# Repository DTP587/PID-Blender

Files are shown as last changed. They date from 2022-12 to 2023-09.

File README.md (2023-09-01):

# PID Blender
_Blender with PID Speed Control, Build Notes. Part of the Open Science Framework repository [OpenLPE](https://osf.io/evupy/)_

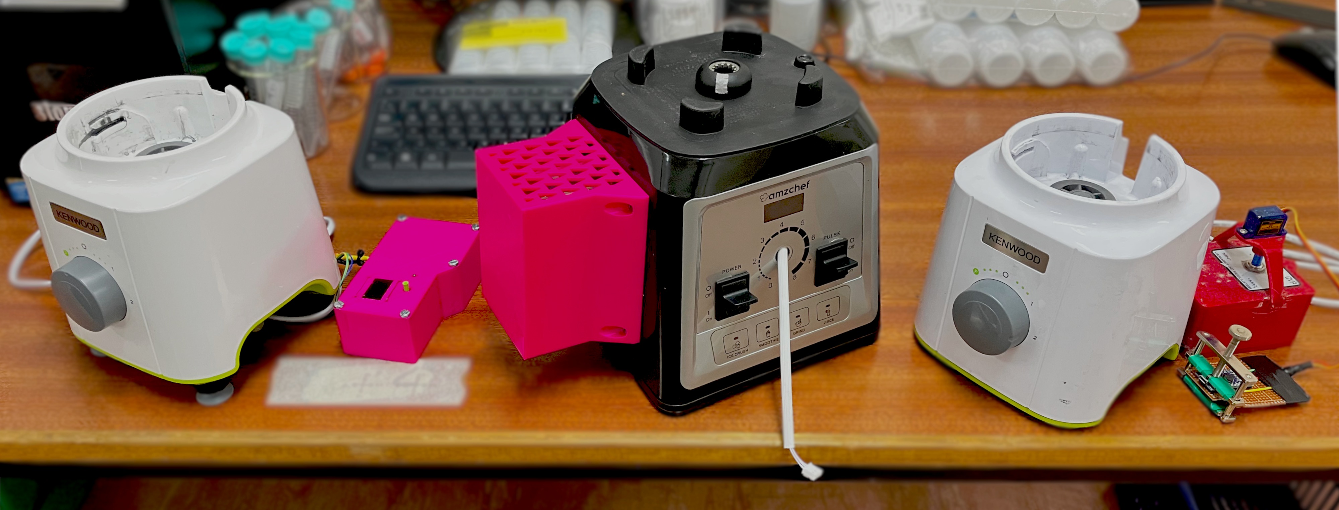
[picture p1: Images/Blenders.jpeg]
Image of all three blenders in order


_From right to left, Dimmer-Blender v1, Dimmer-Blender v2, PID-Blender._

### Background \& Motivation

_This is part of the [OpenLPE](https://osf.io/evupy/) labware project._

For my current work, I needed a blender that could be operated with good control over the exact impeller speed. Initially, I wired dimmer switch into a typical household blender, but found that it was incredibly difficult to maintain the speed accurately and repeatably, especially at low speeds (< $6000$ $rpm$). To improve performance, it was clear what was required was a system that could control the speed dynamically.

The blenders I have been controlling range between $600$ $W$ to $2$ $kW$ peak power, which they can sustain for a maximum of $\approx 1$ $min$ before they get dangerously hot (and melt-y). Some come with automatic sensors to detect when they are overheating and shut-off automatically to save the motor. From my testing, I recommend following the manufacturer's recommendations alternating running it for $1$ $min$ **ON** with a subsequent minimum of $1$ $min$ **OFF** to allow it to cool down.

### Disclaimer!

Playing with AC is _incredibly_ dangerous. Make sure to take all precautions when making modifications and ensure everything is unplugged and grounded.

## Potential Changes

List of changes and whether they have been implemented.

- [ ] The lid to the box doesnt fit the screen perfectly.
- [ ] The $60$ $rpm$ resolution is a bit of a pain at low speeds and could be rectified by switching dynamically between a time-between-counts based approach to measuring speed versus the current counts-within-time.
- [ ] The EMI produced when turning the AC on and off can wreak havoc on the onboard electronics in the box. The arduino needs better isolation from the dimmer module (probably with some well placed tin foil).

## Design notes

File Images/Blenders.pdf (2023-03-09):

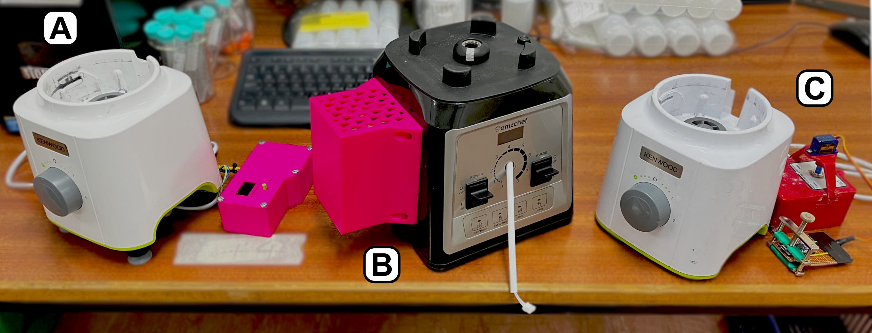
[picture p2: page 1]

A

B

C

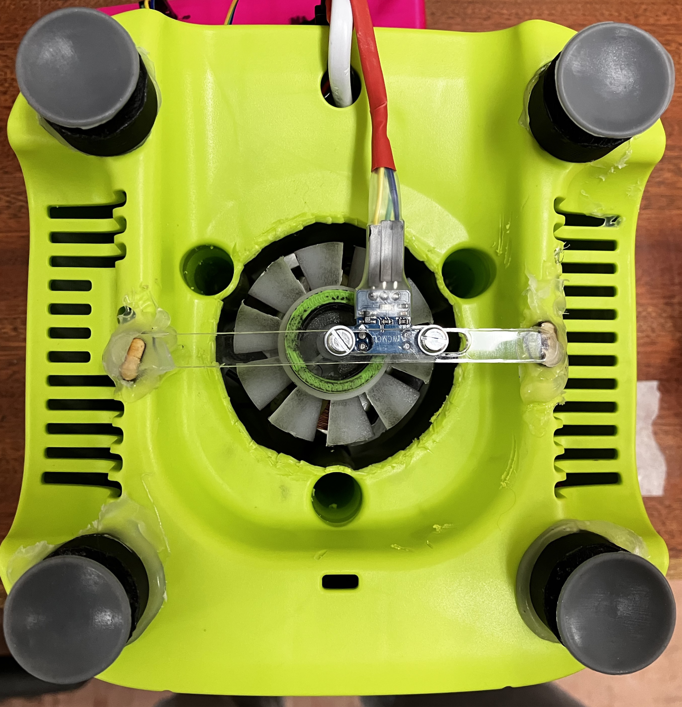
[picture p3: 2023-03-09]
Images/Encoder_Modifications.png

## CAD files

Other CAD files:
CAD/Blender_Box.f3d
CAD/Blender_Feet_Extenders.f3d
CAD/Encoder_Mount.f3d
CAD/Encoder_Ring.f3d

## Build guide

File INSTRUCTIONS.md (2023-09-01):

# Build Instructions and Notes

### Operating Principles

I find that this project has used nearly all the interrupts with this Arduino. It would also be nice if there was some sort of 5V power supply from the blender ([Which is a feature on some of the more pricey models](https://www.amazon.co.uk/Smoothie-AMZCHEF-Commercial-Container-25000RPM/dp/B08CKTB6Z4/ref=sr_1_6?crid=3VN5BPYJ9QWY7&keywords=2000w%2Bblender&qid=1670790024&s=kitchen&sprefix=2000W%2B%2Ckitchen%2C72&sr=1-6&th=1), [or the knock-off alternative](https://www.homgeek.com/p-h22259uk.html), they also have a built-in hall effect sensor).

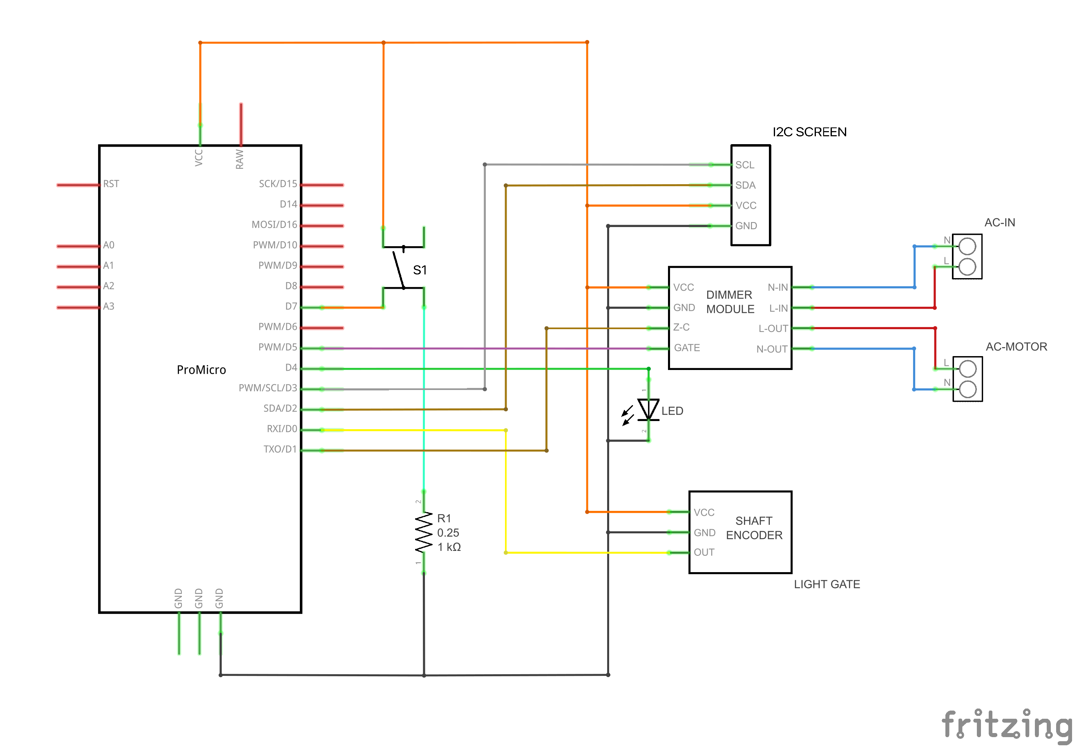
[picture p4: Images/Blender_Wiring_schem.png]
Wiring schematic


This project combines [PID closed loop control](https://www.norwegiancreations.com/2016/08/the-seesaw-part-2-basic-pid-theory-and-arduino-implementation/) with [phase-angle control](https://electricalacademia.com/electronics/scr-thyristor-phase-control-circuit/) of AC signals.

##### Dimmer Module

Passing a signal to the **GATE** pin of the dimmer module passes directly (through an isolating optocoupler) to the gate pin of the TRIAC in the module. 
As the AC signal dips or rises above 0, the Zero Cross signal from the Dimmer module blips high (**Z-C** pin) for a brief period of time.

**L-OUT** then conducts depending on if the TRIAC has been signaled.

##### Shaft Encoder (Photo-interrupter)

**OUT** is high when the light's path is unbroken. When the shaft of the motor is spinning, we repeatedly interrupt the path with an opaque material to recieve a pulsed signal analogous to the motors' current speed.

##### Proportional, Integral \& Differential Control

This control method is favoured for its simplicity, as it only requires tuning a couple of values to control complex signals. A guide for qualitatively tuning PID systems for a good control response can be found [here](https://www.thorlabs.com/newgrouppage9.cfm?objectgroup_id=9013#:~:text=To%20tune%20your%20PID%20controller,to%20roughly%20half%20this%20value.).

## Bill of Materials

|Name               |QTY|Description                           |
|:------------------|:-:|:-------------------------------------|
|[Blender](https://www.kenwoodworld.com/en-gb/blend-x-compact-blp31-d0wg/p/BLP31.D0WG)|1  |600W Kenwood BLP.D0WG|
|[Arduino](https://www.sparkfun.com/products/12640)|1  |Pro Micro (Leonardo based, ATmega32U4)|
|[Dimmer Module](https://www.ebay.co.uk/itm/115506248106?mkevt=1&mkcid=1&mkrid=710-53481-19255-0&campid=5338364432&toolid=11000&_ul=UK&customid=EAIaIQobChMIq-2ml5Py-wIVS57tCh3bXgB5EAQYECABEgJU6vD_BwE&gclid=EAIaIQobChMIq-2ml5Py-wIVS57tCh3bXgB5EAQYECABEgJU6vD_BwE)|1  |Dimmer circuit with optocoupler to isolate live AC from the arduino.|
|Button             |1  |To stop, start and restart processing.|
|LED                |1  |Quick indicator for displaying status.|
|[Light Encoder](https://thepihut.com/products/photo-interrupter-sensor)|1  |For measuring speed, more accurately known as a photo-interrupt sensor. You could easily swap this out with a hall effect sensor.|
|[0.96" OLED I2C Screen](https://www.amazon.co.uk/Display-ARCELI-Characters-Compatible-Raspberry-blue/dp/B09P8DDXZ8/ref=asc_df_B09P8DDXZ8/?tag=googshopuk-21&linkCode=df0&hvadid=570428249641&hvpos=&hvnetw=g&hvrand=12641479531537806638&hvpone=&hvptwo=&hvqmt=&hvdev=c&hvdvcmdl=&hvlocint=&hvlocphy=9045466&hvtargid=pla-1639324494446&psc=1)|1  |For a more detailed readout of the current status.|
|M3 Screws|6  |10 mm long, for holding down the Dimmer and Arduino.|
|M3 Low Profile Screws + Nuts|2  |10 mm long, for holding the Encoder in place.|
|M2.5 Screws + Nuts (Optional)|4  |To keep the Screen bolted onto the lid.|
|M4 Screws (Optional)|5  |10 - 15 mm long, to keep the lid shut on.|
|Blender Box (Optional)|1  |Bottom of the box. To keep the electronics isolated.|
|Button Post (Optional)|1  |Long post so the button can be pressed. Could be replaced by placing the button on the lid.|
|Blender Box Lid (Optional)|1  |Lid of the box.|
|Encoder Cylinder (Optional)|1  |Encoder Cylinder, to hold the Encoder Strip. PLA is transparent to IR.|
|Encoder Strip |1  |One to two Gaps in the encoder strip is the maximum for high speed control (<20'000 rpm)|
|Misc.|   | <ul><li>Hot glue gun or CA glue.</li><li>Wiring and heat shrink</li><li>Soldering Iron</li><li>AC can be quite dangerous, so its best to keep them away by encasing them in an electronics box. f3d files from this project are included in the folder labeled CAD feel free to use it or make your own.</li></ul>|

## Mods

The only modification required to the blender is to mount the encoder. Cutting out a small section of plastic at the bottom of the green plastic shell gives enough access to the motor shaft. The encoder ring provided in the CAD folder fits snuggly within the fan of this blender, and can fit a small section of IR-Opaque strip of material (Sandpaper can do this in a pinch).

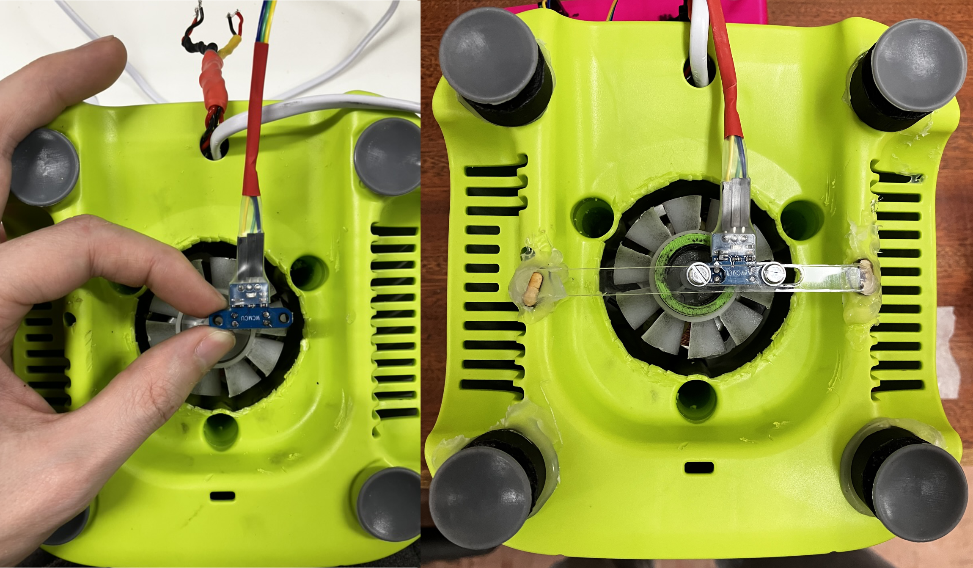
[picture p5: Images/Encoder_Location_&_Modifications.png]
Modifications For Encoder


## Wiring

### Cracking the Blender

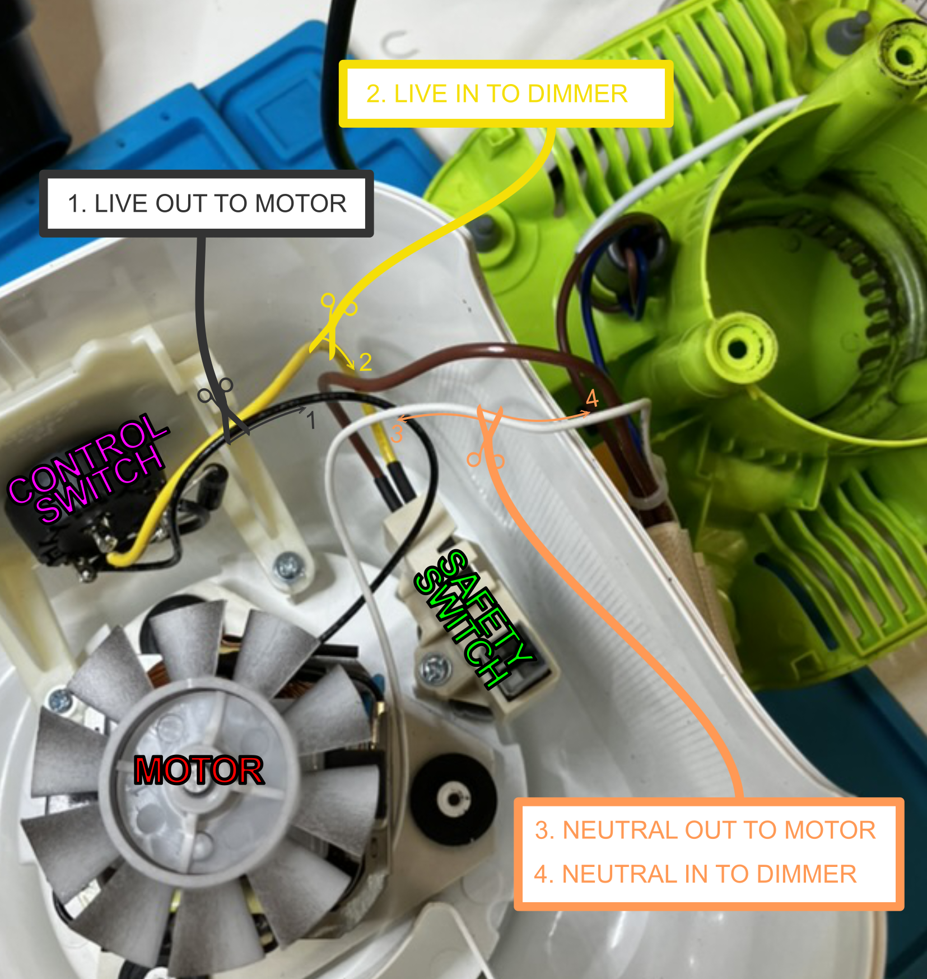
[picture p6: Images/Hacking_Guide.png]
Opened blender with labelled modifications


1.	Unsolder the black wire from the motor to the control switch. This lead is the LIVE AC OUT (**L AC-MOTOR**) to the motor.
2. Unsolder the Yellow Wire from the control switch. This is the LIVE AC IN (**L AC-IN**) to the dimmer.
    
    At this point, the control switch is completely bypassed, but the safety switch isn't. I prefer to keep the safety switch wired in, as it ensures the blender is not live when the jug isnt plugged in.
    
    During my testing, position "P" and "2" on the dial were a simple on off switch (for full AC Power), while position "1" cut the negative half of the waveform.
    
3. The white wire is neutral mains, wired directly to the motor. Cut the wire roughly halfway. This is NEUTRAL AC OUT (**N AC-MOTOR**) to the motor.
4. The other side of the wire cut cut in step 3 is NEUTRAL AC IN (**N AC-IN**) to the Dimmer.

You'll need about half a meter of suitable guage wiring to extend these wires out of the blender. These will take a bit of current, so ensure they are soldered well.

### Wiring the Box

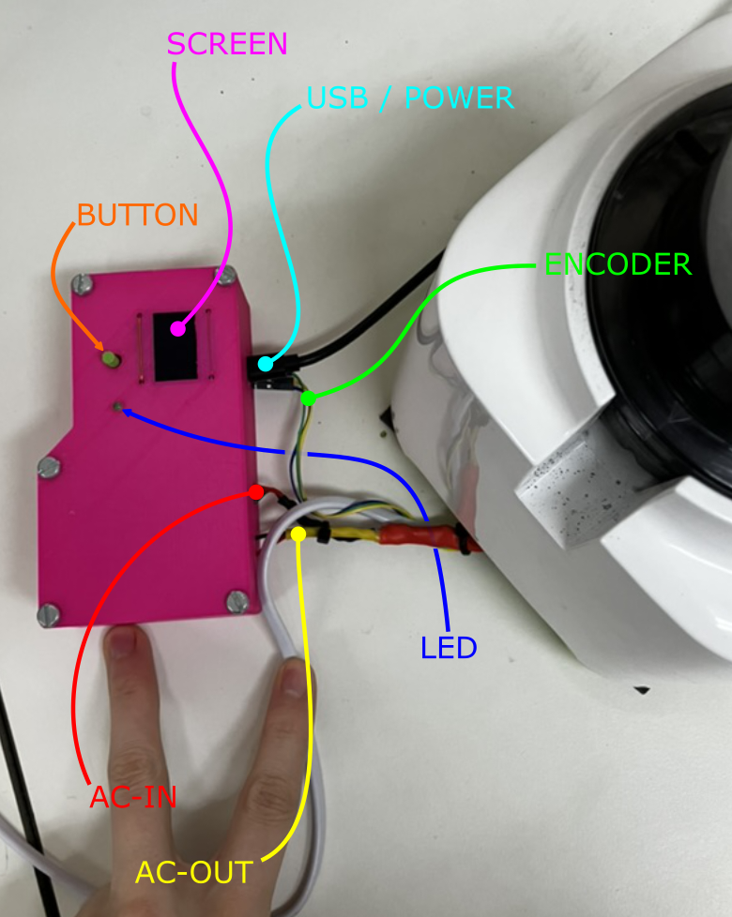
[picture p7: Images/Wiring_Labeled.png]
Wiring into the Electronics box


This is how I set up my box, with the AC Dimmer mounted towards the bottom of the image and the arduino underneath the screen.

## Arduino Code

In this section, I'll comment on the overarching function of the arduino code in `/Arduino Sketches/Pink_Box_v2/Pink_Box_v2.ino`. This contains a routine which runs the blender on and off for the specified amount of time defined at the top of the file.

It is important to stress that interrupt service routines are essential, but also the hardest bit about the project. As `millis()` and `micros()` wont update whilst in the interrupt, and hence mess with the on/off timing which we need to keep accurate. More importantly though, the AC signal requires dimming once every half period of AC ( $10$ $ms$ - $17$ $ms$ ). In summary then, our loop needs to be fast enough to:

- Tell the time
- Read the encoder speed
- Calculate the control signal

And finally,

- Signal the dimmer

All within the $10$ $ms$ between the Zero-Cross signal. The pro micro has a clock speed of $16$ $MHz$, with mains AC being $50$ - $60$ $Hz$, which comes to $160'000$ operations between each Zero-Cross. In context, one division operation takes $\approx 2'000$ clock cycles to compute (division is notoriously slow, [this now defunct blogpost explained it really well](http://www.engblaze.com/faster-code-fridays-understand-division-and-speed-of-operations/)). This turns out to not be enough time to output to the Screen, for instance.

### Encoder Signal

Beginning with the encoder, we trigger the following function on the on a `RISING` edge of the encoder signal.

```
void UpdateCount() {
  COUNT++;
}
```

Reading the number of counts (Stored in `COUNT` and read into `READ_COUNT`) between every $1000$ $ms$ gives us an indication of the speed with a resolution of ± $60$ $rpm$ with a single encoder gap. The maximum feasible number of encoder gaps for this setup seems to be between two and three ( ± $30$ - $20$ $rpm$ resolution). You'll find this beginning at line 217:

```
// Update speed measurement every xxx ms
if (READ_TIME >= 1000) {
OMEGA = ((60*1E3*READ_COUNT)/READ_TIME);

// check for nan values
if (!OMEGA) {
  OMEGA = 0;
  }

Serial.println(OMEGA);
```

We also check the value is a number, as it is sometimes `NAN` when the count is $0$ (i.e. the motor is stopped).

### Dimmer Module

Next is the Zero-Cross interrupt; In this one, we have to do a couple more things than before.

```
void zeroCrossISR() {
  digitalWrite(AC_LOAD, LOW);
  ZERO_STATE[1] = micros();
  ZERO_STATE[0] = 1E3;
}
```
Firstly, we begin by setting the gate pin of the TRIAC (`AC_LOAD`) to `LOW`, which ensures we don't prematurely open the taps to AC straight away. We then take note of the time and set a flag. In our main loop then, we action this at line 242:

```
// Update TRIAC if needed
if (ZERO_STATE[0] == 1E3) {
  ZERO_STATE[2] = micros() - ZERO_STATE[2];
  if (ZERO_STATE[2] >= dim_time) {
    digitalWrite(AC_LOAD, HIGH);   // triac On
    if (ZERO_STATE[2] >= (dim_time + 10)) {
      digitalWrite(AC_LOAD, LOW);  // triac Off
      ZERO_STATE[0]=0;
      }
    }
  }
```
Evaluate the Zero-Cross flag, which when true, we calculate the time since the Zero-Cross was triggered. Once the time reaches the `DIM_TIME` calculated by the PID Control loop, we trigger the gate of the TRIAC to allow the AC to flow. Finally, after a short propogation period ( $10$ $\mu s$ ) for the TRIAC to trigger, the gate is set LOW and the Zero-Cross flag is reset, ready for the next signal from the dimmer.

### PID Control

Next up, we'll look briefly at how the PID control loop is implemented:

**Line 61**

```
// Dimming time
unsigned int SET_POINT = constrain(
    pow((11782 - SET_OMEGA)/2.0849E-8, 0.33317),  // Approximate DIM_TIME
    5, 8000 // min and max
    );  // Dimming 8000 off 5 on
```
To help the PID control find the correct set point, we run a quick approximation to a nearby vlaue using the equation:

$$\left(\frac{1.1782\times 10^4 - \Omega}{2.0849\times 10^{-8}}\right)^{3.3317\times 10^{-1}}$$

Which looks like this:

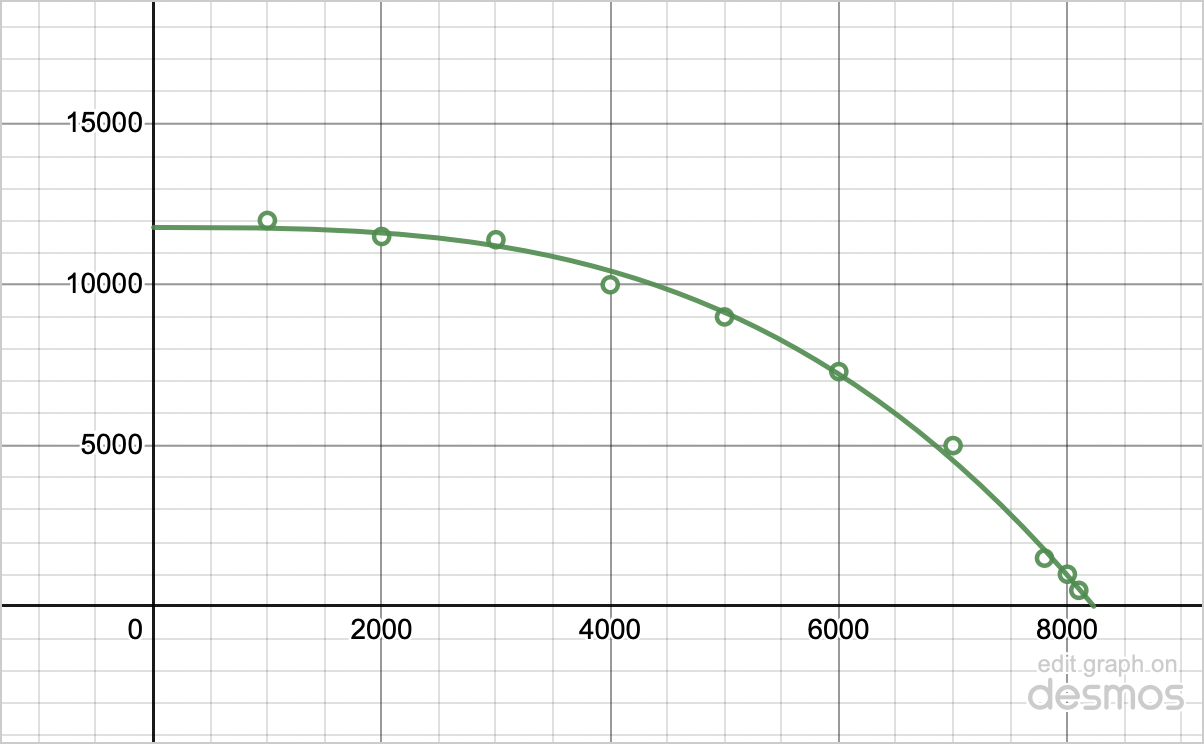
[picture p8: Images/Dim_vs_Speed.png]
<iframe src="https://www.desmos.com/calculator/y3etjdybc4?embed" width="600" height="370" style="border: 1px solid #ccc" frameborder=0></iframe>


**Line 228**

```
PID_ERROR[0]  = OMEGA - SET_OMEGA;        // Proportional
PID_ERROR[1] += PID_ERROR[0] * READ_TIME; // Integral
PID_ERROR[1]  = constrain(PID_ERROR[1], /*min*/, /*max*/);
PID_ERROR[3]  = (PID_ERROR[0] - PID_ERROR[4]);
PID_ERROR[2]  = (abs(PID_ERROR[3])<1E-3) ? 0 : PID_ERROR[3]; // Differential
PID_ERROR[3] = PID_ERROR[0];

control_signal = (1/READ_TIME)*(/*kp*/*PID_ERROR[1] + /*ki*/*PID_ERROR[2] + /*kd*/*PID_ERROR[3]);
dim_time  = constrain(SET_POINT + control_signal, 5, 8000);
```
With our current error being the difference between our measured and target speed, integral error being our current error multiplied by our time between measurements and our differential being the difference between our current error and our previous error divided by our time between measurements, we can proportionally add these together in just the right quantities to control our `dim_time` signal. Constraining the signal helps to avoid the situation where the PID signal flies too far either way in an uncontrollable way.

### Output

The current speed (`OMEGA`) is outputted directly to serial. A typical working cycle would look something like:

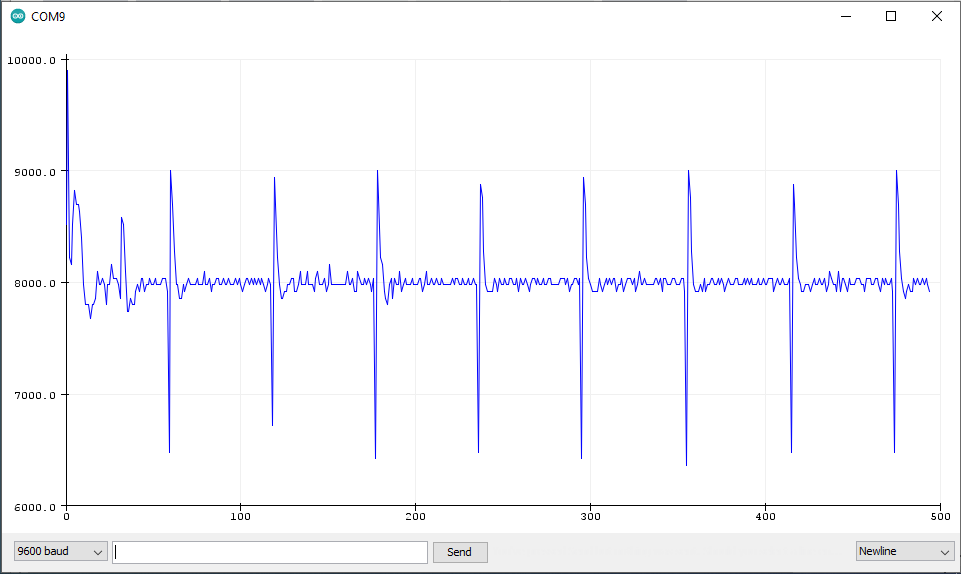
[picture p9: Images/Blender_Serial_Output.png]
Blender performance


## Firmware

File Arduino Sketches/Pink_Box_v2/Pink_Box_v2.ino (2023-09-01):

#include <Arduino.h>

// ------------------ Defines -------------------

#define LIGHT_GATE  0 // Light gate digital input
#define ZERO_PIN    1 // Interrupt to zero cross detection source.
#define LED_PIN     4 // LED pin output.
#define BUTTON_PIN  7 // Button pin.
#define AC_LOAD     5 // Output to Opto-Triac GATE pin.

#define TOTAL_TIME  5     // Minutes, total time on + off
#define ON_TIME     10   // Seconds, on time
#define OFF_TIME    10    // Seconds, off time
#define SET_OMEGA   10000 // RPM 1000 min, 20000 max

// ------------------ Screen -------------------

#include <SPI.h>
#include <Wire.h>
#include <Adafruit_GFX.h>
#include <Adafruit_SSD1306.h>

// Screen information
#define SCREEN_ADDRESS 0x3C
#define SCREEN_WIDTH 128 // OLED display width, in pixels
#define SCREEN_HEIGHT 64 // OLED display height, in pixels
#define OLED_RESET    -1 // Reset pin # (or -1 if sharing Arduino reset pin)

Adafruit_SSD1306 display(SCREEN_WIDTH, SCREEN_HEIGHT, &Wire, OLED_RESET);

void displayMessage(Adafruit_SSD1306 &display, String MESSAGE, int TIME_SO_FAR) {
  // Display initial text
  display.clearDisplay();
  display.setTextSize(2); // 2x Size
  display.setTextColor(SSD1306_WHITE); // Draw white text
  display.setCursor(0,0); // Start at top-left corner
  
  display.println(MESSAGE);
  display.setTextSize(1); // Normal 1:1 pixel scale
  display.println(F("---------------------"));
  
  display.print(F("On  time: ")); display.print(ON_TIME); display.println(F(" s"));
  display.print(F("Off time: ")); display.print(OFF_TIME); display.println(F(" s"));
  display.print(F("In Total: ")); display.print(TIME_SO_FAR); display.print("/"); display.print(TOTAL_TIME); display.println(F(" m"));
  display.println(F("---------------------"));

  display.setTextSize(1);
  display.print(F("Target:   ")); display.print(SET_OMEGA); display.println(F(" rpm"));
  display.display();
  }

// ----------------------------------------------

// Speed counter
volatile int COUNT;
// ZERO_CROSS_FLAG, ZERO_START_TIME, ZERO_READ_TIME
volatile unsigned int ZERO_STATE[3];
// Button flag
volatile bool BUTTON_FLAG = false;
// Button timer
volatile long BUTTON_TIME;

unsigned int SET_POINT = constrain( // LARGE JUG
    pow((11782 - SET_OMEGA)/2.0849E-8, 0.33317),  // Approximate dim_time
    7000, 8000 // min and max
    );  // Dimming 8000 off 5 on
unsigned int control_signal, dim_time;

unsigned int START_COUNT;
unsigned int START_TIME;
unsigned int READ_COUNT;
unsigned int READ_TIME;

float  PID_ERROR[4];
float OMEGA;

// ----------------------------------------------

void zeroCrossISR() {
  digitalWrite(AC_LOAD, LOW);
  ZERO_STATE[1] = micros();
  ZERO_STATE[0] = 1E3;
}

void UpdateCount() {
  COUNT++;
}

void interruptISR() {
  if (BUTTON_FLAG == false) {
    BUTTON_TIME = millis() - BUTTON_TIME;
    if (BUTTON_TIME > 200) {
      Serial.println("Button Triggered");
      BUTTON_FLAG = true;
    }
  }
  else if (BUTTON_FLAG == true) {
    // skip
  }
  BUTTON_TIME = millis();
}

int ReadCount() {
  return COUNT;
}

// ----------------------------------------------


long millisSince(long TIME) {
  return (millis()-TIME);
  }

long roundMillisSince(long TIME) {
  return floor(millisSince(TIME));
  }

bool gapTimeIsReached(unsigned int GAP_TIME, long START_TIME) {
  return (roundMillisSince(START_TIME) >= GAP_TIME*1E3);
  }

float isTotalRuntimeReached(long TIME) {
  return (roundMillisSince(TIME) < (60E3*TOTAL_TIME));
  }

// ------------------- routine ------------------



// ==============================================

void setup() {

  Serial.begin(9600);

  // SSD1306_SWITCHCAPVCC = generate display voltage from 3.3V internally
  if(!display.begin(SSD1306_SWITCHCAPVCC, SCREEN_ADDRESS)) {
    Serial.println(F("SSD1306 allocation failed"));
    for(;;); // Don't proceed, loop forever
  }
  
  pinMode(AC_LOAD, OUTPUT);   // Set AC Load pin as output
  digitalWrite(AC_LOAD, LOW); // triac On
  pinMode(LED_PIN, OUTPUT);   // LED pin output
  digitalWrite(BUTTON_PIN, HIGH); // Set button high
  
  attachInterrupt( // Check whether signal is rising
    digitalPinToInterrupt(ZERO_PIN),
    zeroCrossISR,
    RISING
  );

  attachInterrupt(
    digitalPinToInterrupt(LIGHT_GATE),
    UpdateCount,
    RISING
  );

  attachInterrupt(
    digitalPinToInterrupt(BUTTON_PIN),
    interruptISR,
    LOW
  );
}

// ----------------------------------------------

void loop() {

  unsigned int GAP_TIME = 0;
  unsigned int ON_COUNTER = 0;
  unsigned int OFF_COUNTER = 0;
  unsigned int TARGET = 0;
  unsigned int SPEED_READ_COUNTER = 0;

  displayMessage(display, "CONNECTED", 0);
  
  while (!BUTTON_FLAG) {
    // Do nothing
    }
  BUTTON_FLAG = false;


  displayMessage(display, "PROCESSING", 0);
  delay(1000);

  unsigned long START_ROUTINE_TIME = millis();
  
  // This loop needs to stay FAST, no display commands!
  while (isTotalRuntimeReached(START_ROUTINE_TIME)) {
    
    if (gapTimeIsReached(GAP_TIME, START_ROUTINE_TIME)) {

      if (OFF_COUNTER >= ON_COUNTER) {
        
        // Display on message

        TARGET = SET_OMEGA;

        START_COUNT = COUNT;
        START_TIME  = millis();
        SPEED_READ_COUNTER = 0;

        digitalWrite(LED_PIN, HIGH);
        ON_COUNTER += 1;
        }

      else if (OFF_COUNTER < ON_COUNTER) {

        // Display off message
        displayMessage(display, "PROCESSING", GAP_TIME/60);
        TARGET = 0;

        digitalWrite(LED_PIN, LOW);
        OFF_COUNTER += 1;
        }
      
      GAP_TIME = ON_TIME*ON_COUNTER + OFF_TIME*OFF_COUNTER;
      }

    // Check for external interrupt.
    if (BUTTON_FLAG) {
      digitalWrite(LED_PIN, LOW);
      break;
    }

    // Speed control if on.
    if (TARGET == SET_OMEGA) {
      READ_TIME  = millis() - START_TIME;
      READ_COUNT = ReadCount() - START_COUNT;
      
      // Update speed measurement every xxx ms
      if (READ_TIME >= 1000) {
        OMEGA = ((60*1E3*READ_COUNT)/READ_TIME);
        
        // check for nan values
        if (!OMEGA) {
          OMEGA = 0;
        }
        else if ((SPEED_READ_COUNTER < 1) && (ON_COUNTER > 1)) {
          // Pass, don't update for the first cycle after rough angle is found
        }
        else {
          PID_ERROR[0]  = OMEGA - SET_OMEGA; // Proportional
          PID_ERROR[1] += PID_ERROR[0];      // Integral
          PID_ERROR[1] = constrain(PID_ERROR[1], /*min*/, /*max*/)
                                             // Differential
          PID_ERROR[3]  = (PID_ERROR[0] - PID_ERROR[3]);
          PID_ERROR[2]  = (abs(PID_ERROR[3])<1E-3) ? 0 : PID_ERROR[3];
          PID_ERROR[3]  = PID_ERROR[0];
  
          control_signal = (1/READ_TIME)*(0*PID_ERROR[0] + 0*PID_ERROR[1] + 0*PID_ERROR[2]);
          dim_time  = constrain(SET_POINT+control_signal, 5, 8000);
        }
        
//        Serial.print(dim_time);
//        Serial.print(" ");
        Serial.println(OMEGA);

        SPEED_READ_COUNTER += 1;
        START_COUNT = ReadCount();
        START_TIME  = millis();

      }
    
      // Update TRIAC if needed
      if (ZERO_STATE[0] == 1E3) {
        ZERO_STATE[2] = micros() - ZERO_STATE[1];
        if (ZERO_STATE[2] >= dim_time) {
          digitalWrite(AC_LOAD, HIGH);   // triac On
          if (ZERO_STATE[2] >= (dim_time + 10)) {
            digitalWrite(AC_LOAD, LOW);  // triac Off
            ZERO_STATE[0]=0;
          }
        }
      }
    else if (TARGET == 0) {
      // pass, no call to setSpeed()
      }
    }
  }
  
  if (BUTTON_FLAG) {
    Serial.print("Time on: ");
    Serial.println(millisSince(START_ROUTINE_TIME));
    displayMessage(display, "STOPPED", GAP_TIME/60);
    }
  else if (!BUTTON_FLAG) {
    displayMessage(display, "COMPLETED", TOTAL_TIME);
    }

  BUTTON_FLAG = false;
  while (!BUTTON_FLAG) {
    digitalWrite(LED_PIN, HIGH);
    delay(1);
    digitalWrite(LED_PIN, LOW);
    delay(20);
    }
  
  BUTTON_FLAG = false;
}

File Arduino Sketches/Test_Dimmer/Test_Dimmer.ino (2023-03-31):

/*
Original Uno wiring
Gate = (7, Digital) Sync = (3, PWM)
Looks like the original code was hacked off:
https://www.instructables.com/Arduino-controlled-light-dimmer-The-circuit/
https://en.wikipedia.org/wiki/TRIAC
https://www.youtube.com/watch?v=cyeEzU6KmzY

 +V ▲
    │
    │
    │       ooo ──── 340 Vpp
    │    ooo   ooo
    │  oo         oo
    │ o             o
    │o               o                 20 ms
   0├──────────────────────────────────► t
    │           10 ms o               o
    │                  o             o
    │                   oo         oo
    │                     ooo   ooo
    │                        ooo
    │
    │
 -V ▼  50 Hz ~ 1s/50 = 20 ms

Zero crosses every 1/2 cycle, with each 1/2 cycle lasting 10 ms for 50 Hz
signal.

*/

#define AC_LOAD  5  // Output to Opto-Triac GATE pin.
#define ZERO_PIN 1  // Interrupt to zero cross detection source.

unsigned char dimming = 80;  // Dimming level (0-100) (0 - on, 95 - off)
                             // below 5 there is some flickering

void setup() {
  Serial.begin(9600);
  
  pinMode(AC_LOAD, OUTPUT); // Set AC Load pin as output
  digitalWrite(AC_LOAD, LOW);   // triac On
  
  attachInterrupt( // Check whether signal is rising
    digitalPinToInterrupt(ZERO_PIN),
    zero_crosss_int,
    RISING
  );


}


// function to be fired at the zero crossing to dim the light
void zero_crosss_int() {
  long dimtime = (100*dimming);   // For 60Hz =>65
  Serial.println(dimtime);
  delayMicroseconds(dimtime);    // Off cycle
  digitalWrite(AC_LOAD, HIGH);   // triac On
  delayMicroseconds(10);
  digitalWrite(AC_LOAD, LOW);    // triac Off
}



void loop() {
}

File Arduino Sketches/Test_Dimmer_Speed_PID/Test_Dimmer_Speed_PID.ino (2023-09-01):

#define AC_LOAD  5   // Output to Opto-Triac GATE pin.
#define ZERO_PIN 1   // Interrupt to zero cross detection source.
#define LIGHT_GATE 0 // Light gate digital input

#define SET_SPEED 1000 // Target Speed

unsigned int SET = constrain(
    pow((11782 - SET_SPEED)/2.0849E-8, 0.33317),  // Approximate DIM_TIME
    5, 8000 // min and max
    );  // Dimming 9000 off 50 on
unsigned int control_signal, DIM_TIME;

// Without Control
//8100 - 500
//8000 - 1000
//7800 - 1500
//7000 - 5000
//6000 - 7300
//5000 - 9000
//4000 - 10000
//3000 - 11400
//2000 - 11500


volatile int count;

unsigned int START_COUNT = count;
unsigned int READ_COUNT;
unsigned int START_TIME  = millis();
unsigned int READ_TIME;
float  PID_ERROR[4];

unsigned int ZERO_START_TIME;
unsigned int ZERO_READ_TIME;

bool ZERO_CROSS = false;

float OMEGA;


void zero_cross_void() {
  digitalWrite(AC_LOAD, LOW);
  ZERO_START_TIME = micros();
  ZERO_CROSS = true;
}

void UpdateCount() {
  count++;
}

int ReadCount() {
  return count;
}


void setup() {
  Serial.begin(9600);
  
  pinMode(AC_LOAD, OUTPUT); // Set AC Load pin as output
  digitalWrite(AC_LOAD, LOW);   // triac On
  
  attachInterrupt( // Check whether signal is rising
    digitalPinToInterrupt(ZERO_PIN),
    zero_cross_void,
    RISING
  );

  attachInterrupt(
    digitalPinToInterrupt(LIGHT_GATE),
    UpdateCount,
    RISING
  );

}

void loop() {
  Serial.println("----");

  for (;;) {
    READ_TIME  = millis() - START_TIME;
    READ_COUNT = ReadCount() - START_COUNT;
  
    // Update speed measurement every xxx ms
    if (READ_TIME >= 1000) {
      OMEGA = ((60*1E3*READ_COUNT)/READ_TIME);
      
      // check for nan values
      if (!OMEGA) {
        OMEGA = 0;
        }
  
      // Serial.print(READ_COUNT);
      // Serial.print(" ");
      Serial.println(OMEGA);


      PID_ERROR[0]  = OMEGA - SET_SPEED; // Proportional
      PID_ERROR[1] += PID_ERROR[0]; // Integral
      PID_ERROR[3]  = (PID_ERROR[0] - PID_ERROR[3]);
      PID_ERROR[2]  = (abs(PID_ERROR[3])<1E-3) ? 0 : PID_ERROR[3]; // Differential

      control_signal = (1/READ_TIME)*(0*PID_ERROR[0] + 0*PID_ERROR[1] + 0*PID_ERROR[2]);
      DIM_TIME  = constrain(SET+control_signal, 5, 8000);
      
      START_COUNT = ReadCount();
      START_TIME  = millis();

      PID_ERROR[3] = PID_ERROR[0];
    }
  
    // Update TRIAC if needed
    if (ZERO_CROSS) {
      ZERO_READ_TIME = micros() - ZERO_START_TIME;
      if (ZERO_READ_TIME >= DIM_TIME) {
        digitalWrite(AC_LOAD, HIGH);   // triac On
        if (ZERO_READ_TIME >= (DIM_TIME + 10)) {
          digitalWrite(AC_LOAD, LOW);  // triac Off
          ZERO_CROSS = false;
        }
      }
    }
  }
}
